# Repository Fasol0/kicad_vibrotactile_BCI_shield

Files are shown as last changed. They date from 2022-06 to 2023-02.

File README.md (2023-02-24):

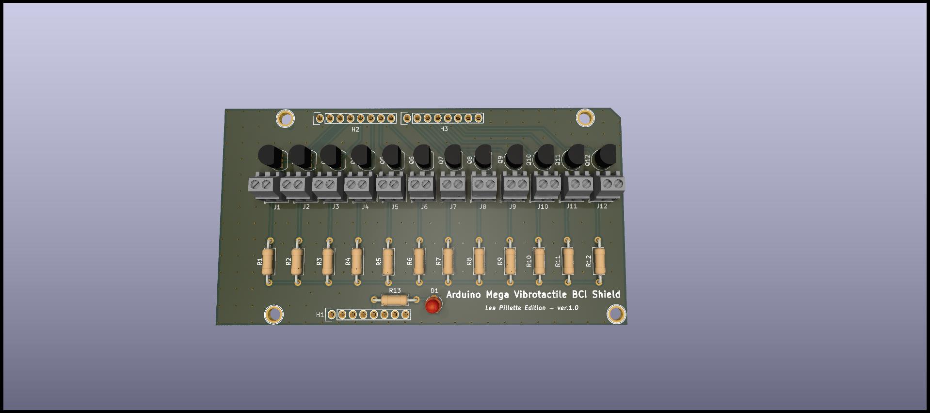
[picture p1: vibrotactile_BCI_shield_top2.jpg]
Vibrotactile BCI Shield


## Printed Circuit board (PCB) settings:

- Dimensions  : 99.06mm x 53.34mm
- Material    : FR-4 TG130
- Layers      : 2
- Thickness   : 1.6mm
- Solder Mask : Green
- Silkscreen  : White
- Finish      : HASL/ENIG
- Vias        : Tenting vias
- Copper      : 1 oz. (All layers) 

### List of some manufacturers:
- PCBGoGo
- UET PCB
- SeeedStudio
- JLCPCB

### HOW TO ORDER:

Go to one of these manufacturers website, then:

#### OPTION 1 - FULL ASSEMBLED BOARD (PCBA):

- Select PCBA (PCB + Assembly) option
- Fill PCB settings
- upload Manufacturing_PCBA.zip

#### OPTION 2 - PCB Only, hand soldering:

- Select PCB option
- Fill PCB settings
- upload Manufacturing_PCB.zip
- buy all components in the BOM_PartType-Vibrotactile BCI shield.xlsx file

these components can be bought from several distributors:
Farnell, RScomponents, Digikey, Mouser, Arrow..

### Note:
N-MOSFETs are often facing shortages. 
if BS170 is not available, it can be replaced by one of these references:
- 2N7000
- BS270
- VN2106N3-G
- VN10KN3-G
- 2N7008-G
- TN2106N3-G
- TN5325N3-G
- ZVN2110A

---

## MOTORS:

2 options:

Fast delivery (1-3 days) :
https://www.amazon.fr/0-3in-moteur-vibration-%C3%A9tanche-masseur/dp/B08CHHMVWY/ref=sr_1_4?crid=2JJ113Z7XVKXU&keywords=moteur+vibrant+7mm&qid=1655198366&s=industrial&sprefix=moteur+vibrant+7mm%2Cindustrial%2C63&sr=1-4

Lowest price (1-2 months) : select the 1.5V to 3.7V version
https://fr.aliexpress.com/item/1005002945728204.html?spm=a2g0o.productlist.0.0.43501c7ajrwj7v&algo_pvid=59802b58-b0c1-436a-8371-263ce5a04aeb&algo_exp_id=59802b58-b0c1-436a-8371-263ce5a04aeb-2&pdp_ext_f=%7B%22sku_id%22%3A%2212000022908295436%22%7D&pdp_npi=2%40dis%21EUR%21%212.32%21%21%212.06%21%21%402100bdd716551982956516490e7309%2112000022908295436%21sea

### Note: 
Picking 1.5V to 5V motors instead would allow a wider vibration range and remove the need of using resistors R1 to R12.
In this case PCB should be updated to remove the resistors slots.
However these motors have higher price (2.32€ vs 1.07€ for the 3.7V version), and are harder to find for fast delivery.

---

## Updates from initial version:

- Changed software from Altium to Kicad (ver. 6)
- PCB dimensions reduced to 99.00 x 53.34mm
- obsolete MOSFET BS170G replaced by BS170
- Motor connectors reference replaced to 282834-2 (smaller footprint, and higher availability)
- Resistors R1 to R12 changed from 6.8 Ohm to 24 Ohm

Motors are rated 3.0V and can go up to 3.7V.  
Current at 3.7V is about 55mA.  
Motors are powered with the 5V rail from the Arduino. Since motors voltage should not exceed 3.7V,  
Resistors R1 to R12 values should be:  
R = DV / I with:  
DV = 5-3.7V = 1.3V  
I = 55mA  
Therefore R = 24 Ohm  

With this setup all motors can safely be driven by PWM from 0 to 100% dutycycle.

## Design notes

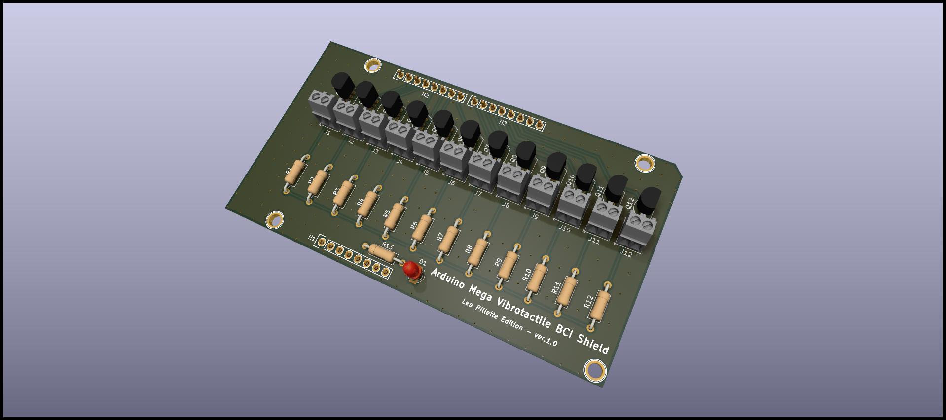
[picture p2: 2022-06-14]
vibrotactile_BCI_shield_top.jpg

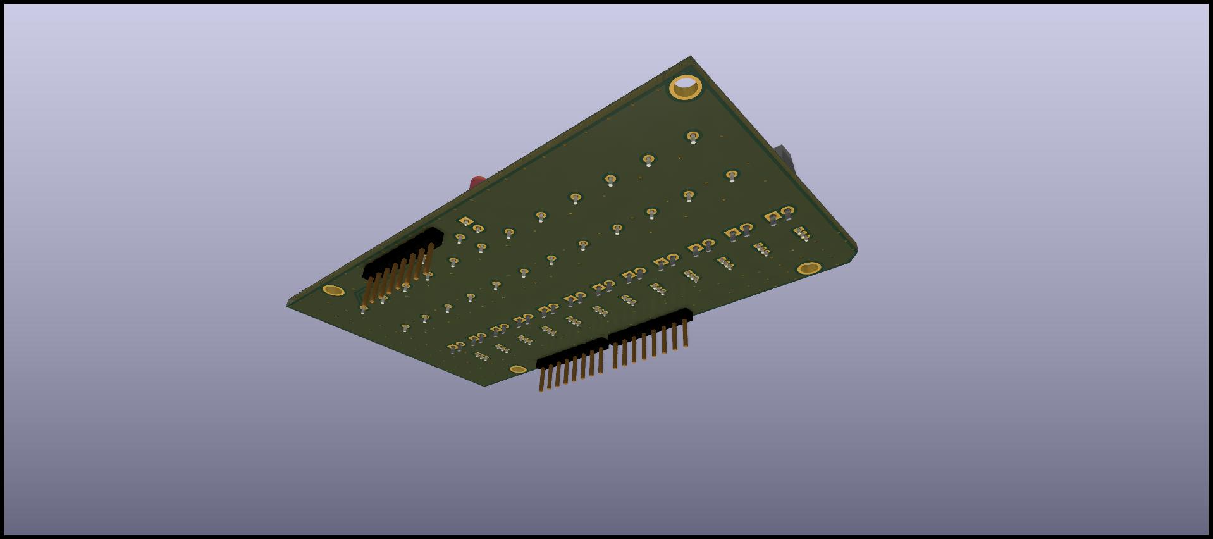
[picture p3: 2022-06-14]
vibrotactile_BCI_shield_bot.jpg

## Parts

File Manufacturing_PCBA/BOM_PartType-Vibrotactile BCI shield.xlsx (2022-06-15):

Designator | Description | Manufacturer Part Number | Manufacturer | Quantity | Octopart URL | Farnell URL | alternative 1 | alternative 2
H1, H2, H3 | Conn Unshrouded Header HDR 8 POS 2.54mm Solder ST Thru-Hole Automotive Bulk | TSW-108-15-L-S | Samtec | 3 | http://octopart.com/tsw-108-15-l-s-samtec-11810720 | https://fr.farnell.com/molex/22-28-4081/conn-header-8-voies-1-rangee-2/dp/3049535?ost=22-28-4081 | 22-28-4081 | M20-9990845
D1 | Grn diffused reflector LED, L1334GT 25mA | L-1334GT | Kingbright | 1 | http://octopart.com/l-1334gt-kingbright-55391525 | https://fr.farnell.com/kingbright/l-1334gt/reflecteur-led-3mm-green/dp/2001636
Q1, Q2, Q3, Q4, Q5, Q6, Q6, Q7, Q8, Q9, Q10, Q11, Q12 | Small Signal MOSFET, 500 mA, 60 V, N-Channel, 3-Pin TO-92, Pb-Free, Bulk Box | BS170 | OnSemi | 12 | https://octopart.com/search?q=BS170&currency=USD&specs=0 | https://fr.farnell.com/microchip/vn2106n3-g/d-mosfet-canal-n-0-3a-60v-to-92/dp/2851591
M1, M2, M3, M4, M5, M6, M7, M8, M9, M10, M11, M12 | Wire to Board 2 Position 2.54 mm Pitch 30-16 AWG Terminal Block | 282834-2 | TE Connectivity | 12 | https://octopart.com/search?q=282834-2&currency=USD&specs=0 | https://fr.farnell.com/buchanan-te-connectivity/282834-2/terminal-block-pcb-30-16awg-2/dp/2112482?st=282834-2
R13 | Metal Film Resistors 150 Ohm 3/5W 50PPM | LR1F150R | TE Connectivity | 1 | https://octopart.com/search?autosugg_idx=0&currency=USD&oq=LR1F150R&q=LR1F150R&specs=1 | https://fr.farnell.com/te-connectivity/lr1f150r/resistance-metal-150r-0-6w-1/dp/2330020?ost=lr1f150r
R1, R2, R3, R4, R5, R6, R7, R8, R9, R10, R11, R12 | Metal Film Resistors 24 Ohm 3/5W 50PPM | LR1F24R | TE Connectivity | 12 | https://octopart.com/search?autosugg_idx=0&currency=USD&oq=LR1F24R&q=LR1F24R&specs=1 | https://fr.farnell.com/te-connectivity/lr1f24r/resistance-metal-24r-0-6w-1/dp/2330078?ost=lr1f24r

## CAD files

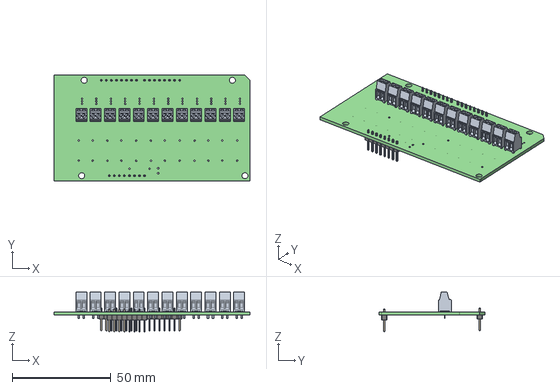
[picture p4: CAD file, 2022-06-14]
vibrotactile_BCI_shield/vibrotactile_BCI_shield.step
99.1 x 53.3 x 20.0 mm
vibrotactile_BCI_shield PCB

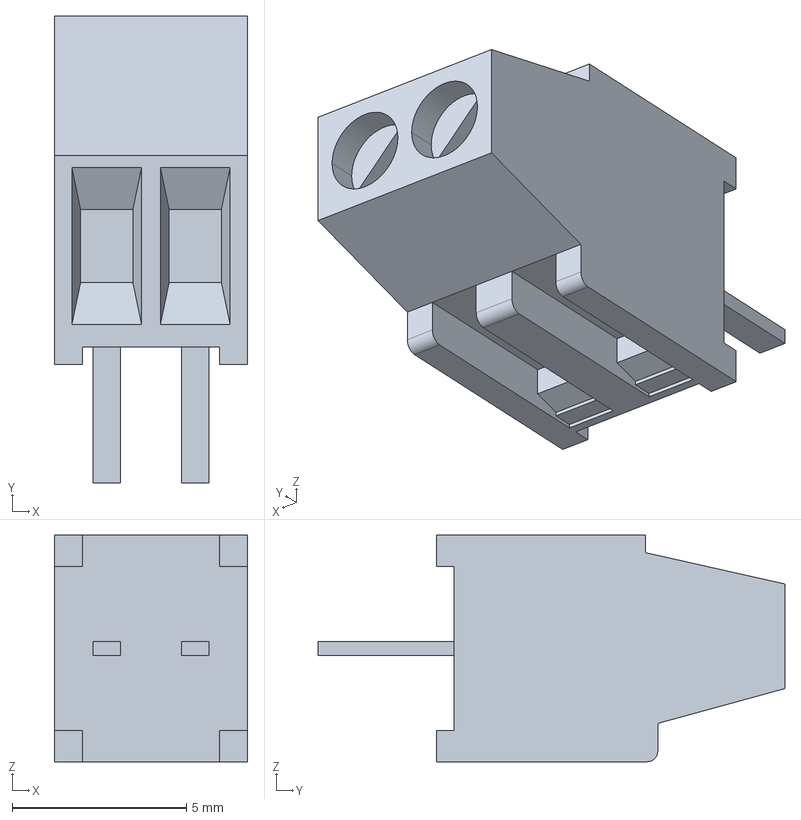
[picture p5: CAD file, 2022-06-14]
vibrotactile_BCI_shield/Components_3D/282834-2--3DModel-STEP-1.STEP
5.54 x 13.4 x 6.50 mm

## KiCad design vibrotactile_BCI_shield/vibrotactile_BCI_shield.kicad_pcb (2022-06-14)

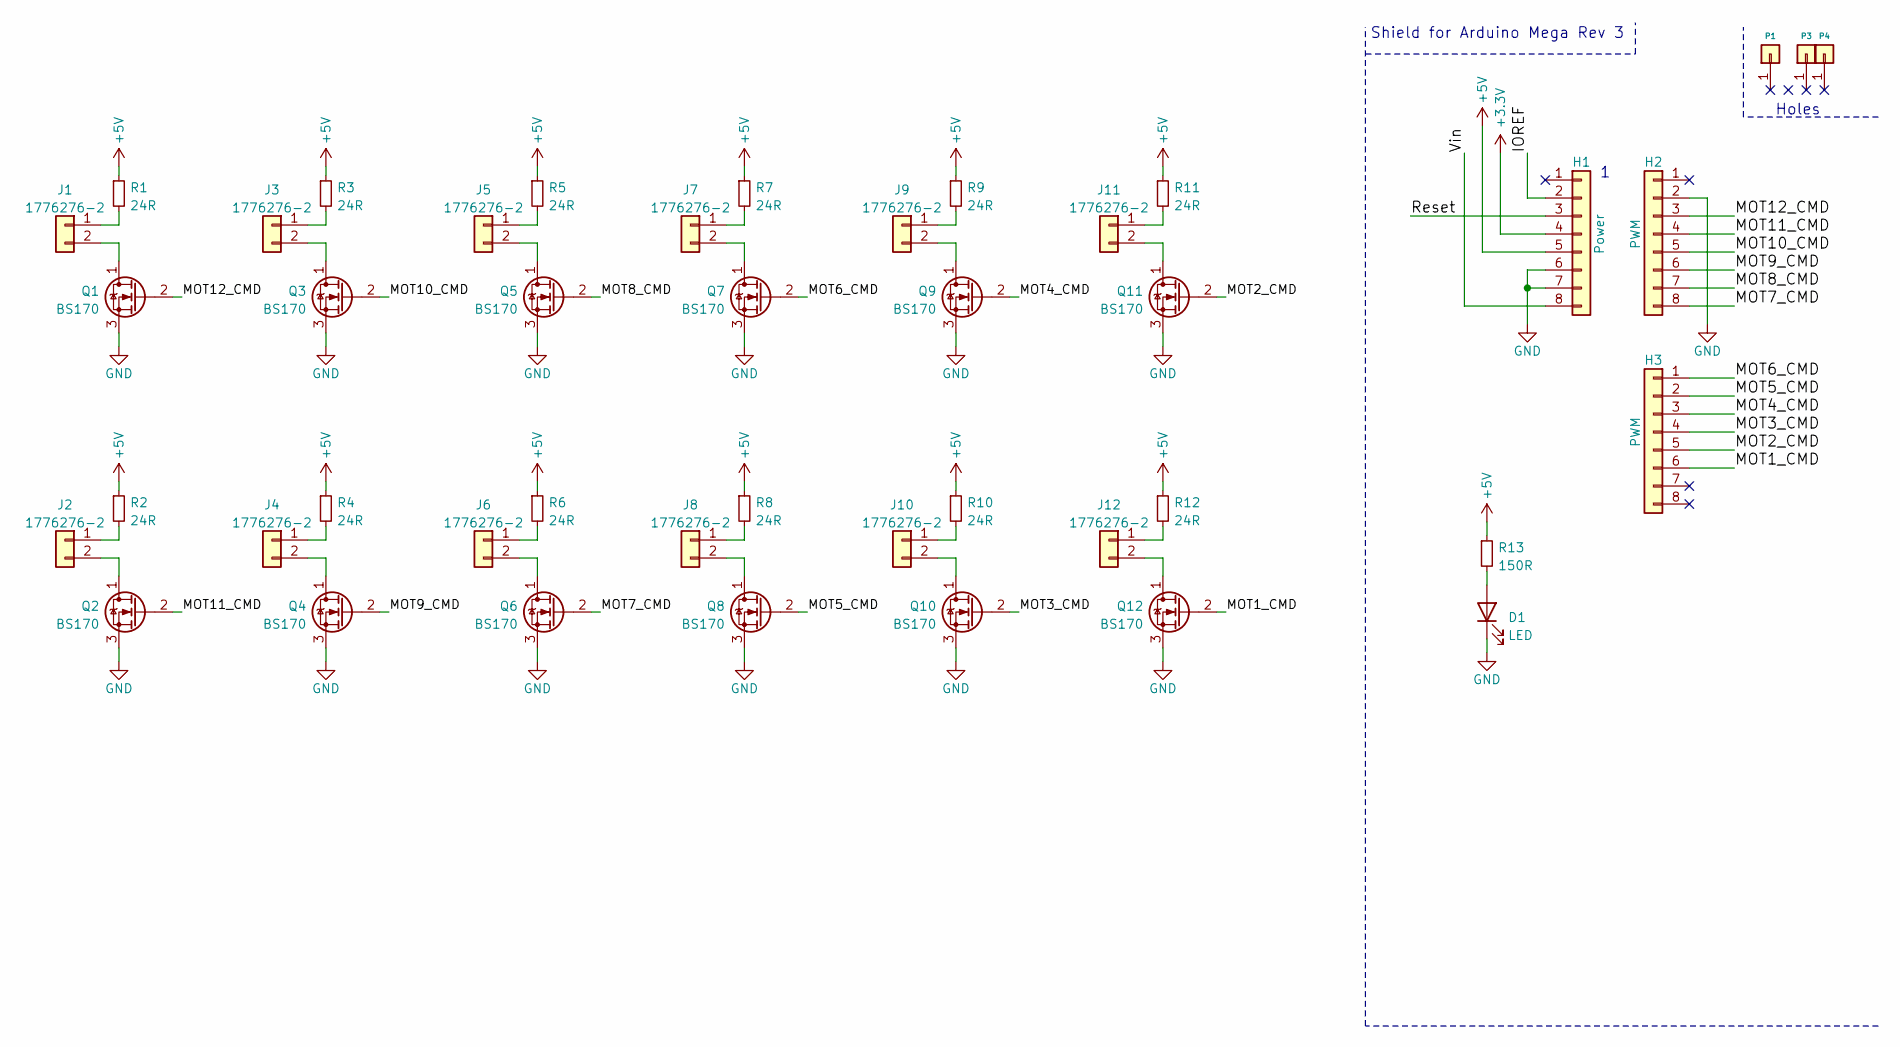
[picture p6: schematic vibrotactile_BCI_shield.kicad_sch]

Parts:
D1: LED; LED_D3.0mm
H1: Power; Socket_Strip_Arduino_1x08
H2, H3: PWM; Socket_Strip_Arduino_1x08
J1, J2, J3, J4, J5, J6, J7, J8, J9, J10, J11, J12: 1776276-2; TE_Connectivity282834-2
P1, P3, P4: CONN_01X01; Arduino_1pin
Q1, Q2, Q3, Q4, Q5, Q6, Q7, Q8, Q9, Q10, Q11, Q12: BS170; TO-92_Inline
R1, R2, R3, R4, R5, R6, R7, R8, R9, R10, R11, R12: 24R; R_Axial_DIN0207_L6.3mm_D2.5mm_P10.16mm_Horizontal
R13: 150R; R_Axial_DIN0207_L6.3mm_D2.5mm_P10.16mm_Horizontal

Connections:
+3V3: H1.4
+5V: H1.5, R1.1, R2.1, R3.1, R4.1, R5.1, R6.1, R7.1, R8.1, R9.1, R10.1, R11.1, R12.1, R13.1
/IOREF: H1.2
/MOT1_CMD: H3.6, Q12.2 (G)
/MOT2_CMD: H3.5, Q11.2 (G)
/MOT3_CMD: H3.4, Q10.2 (G)
/MOT4_CMD: H3.3, Q9.2 (G)
/MOT5_CMD: H3.2, Q8.2 (G)
/MOT6_CMD: H3.1, Q7.2 (G)
/MOT7_CMD: H2.8, Q6.2 (G)
/MOT8_CMD: H2.7, Q5.2 (G)
/MOT9_CMD: H2.6, Q4.2 (G)
/MOT10_CMD: H2.5, Q3.2 (G)
/MOT11_CMD: H2.4, Q2.2 (G)
/MOT12_CMD: H2.3, Q1.2 (G)
/Reset: H1.3
/Vin: H1.8
GND: D1.1 (K), H1.6, H1.7, H2.2, Q1.3 (S), Q2.3 (S), Q3.3 (S), Q4.3 (S), Q5.3 (S), Q6.3 (S), Q7.3 (S), Q8.3 (S), Q9.3 (S), Q10.3 (S), Q11.3 (S), Q12.3 (S)
unnamed: D1.2 (A), R13.2
unnamed: J1.1, R1.2
unnamed: J1.2, Q1.1 (D)
unnamed: J2.1, R2.2
unnamed: J2.2, Q2.1 (D)
unnamed: J3.1, R3.2
unnamed: J3.2, Q3.1 (D)
unnamed: J4.1, R4.2
unnamed: J4.2, Q4.1 (D)
unnamed: J5.1, R5.2
unnamed: J5.2, Q5.1 (D)
unnamed: J6.1, R6.2
unnamed: J6.2, Q6.1 (D)
unnamed: J7.1, R7.2
unnamed: J7.2, Q7.1 (D)
unnamed: J8.1, R8.2
unnamed: J8.2, Q8.1 (D)
unnamed: J9.1, R9.2
unnamed: J9.2, Q9.1 (D)
unnamed: J10.1, R10.2
unnamed: J10.2, Q10.1 (D)
unnamed: J11.1, R11.2
unnamed: J11.2, Q11.1 (D)
unnamed: J12.1, R12.2
unnamed: J12.2, Q12.1 (D)

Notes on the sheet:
Holes
Shield for Arduino Mega Rev 3

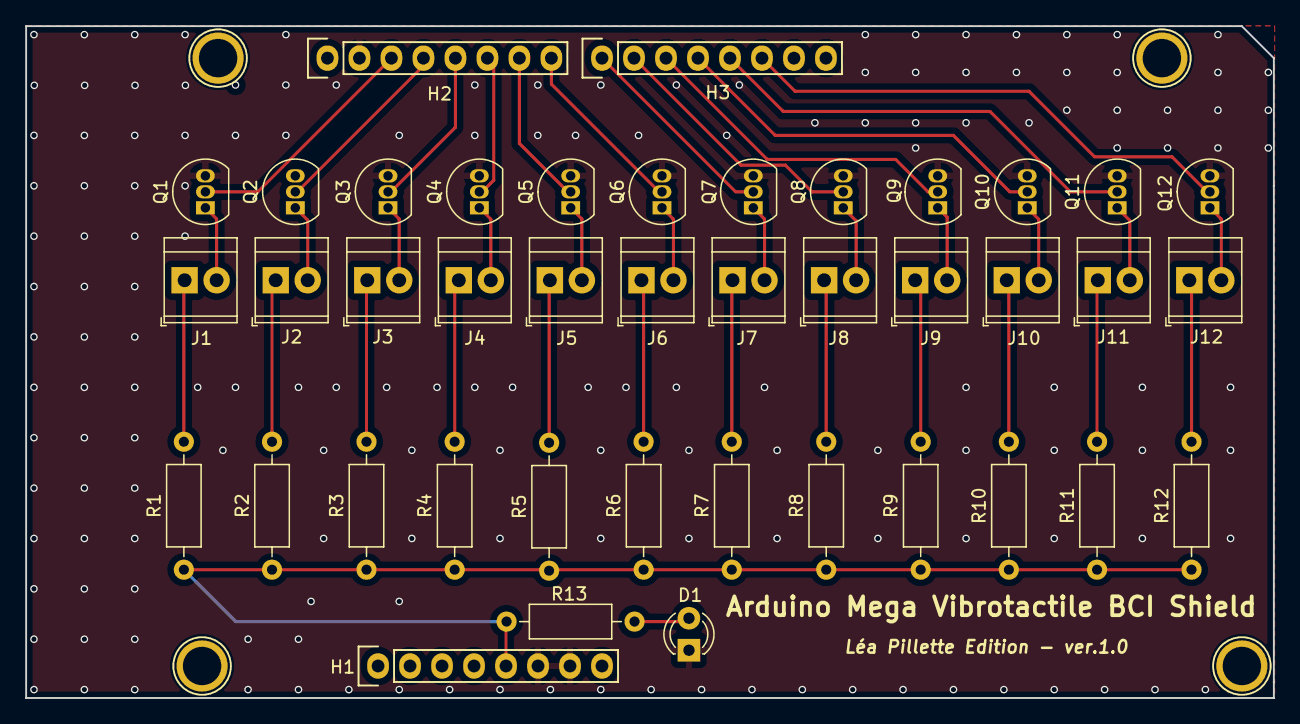
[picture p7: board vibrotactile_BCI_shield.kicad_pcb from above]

Board: 2 copper layers, 99.1 x 53.3 mm, 45 parts (0 on the bottom side), 39 nets.

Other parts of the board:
P2: CONN_01X01; Arduino_1pin

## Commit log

2022-06-14 prod files
    [BOM_PartType-Vibrotactile BCI shield.xlsx, vibrotactile_BCI_shield-B_Cu.gbr, vibrotactile_BCI_shield-B_Silkscreen.gbr, vibrotactile_BCI_shield-F_Cu.gbr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]
2022-06-15 alternative headers
    [BOM_PartType-Vibrotactile BCI shield.xlsx]
2022-06-15 adding farnell ref
    [BOM_PartType-Vibrotactile BCI shield.xlsx]
2022-06-20 adding missing gerbers
    [vibrotactile_BCI_shield-B_Cu.gbr, vibrotactile_BCI_shield-B_Mask.gbr, vibrotactile_BCI_shield-B_Silkscreen.gbr, vibrotactile_BCI_shield-Edge_Cuts.gbr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]
